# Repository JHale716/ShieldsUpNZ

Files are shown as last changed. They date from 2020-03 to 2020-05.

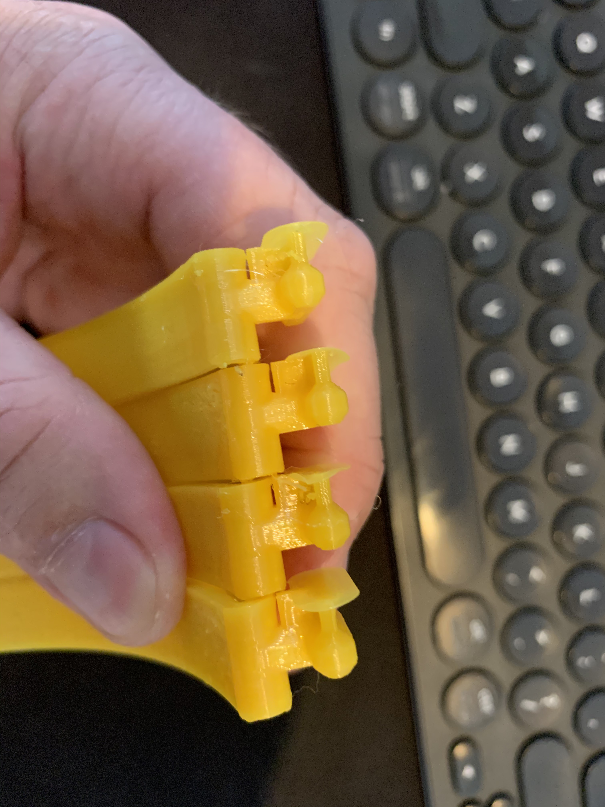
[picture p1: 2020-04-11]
6. Images/Ender3 Printing/V2 Support gap 1.jpeg

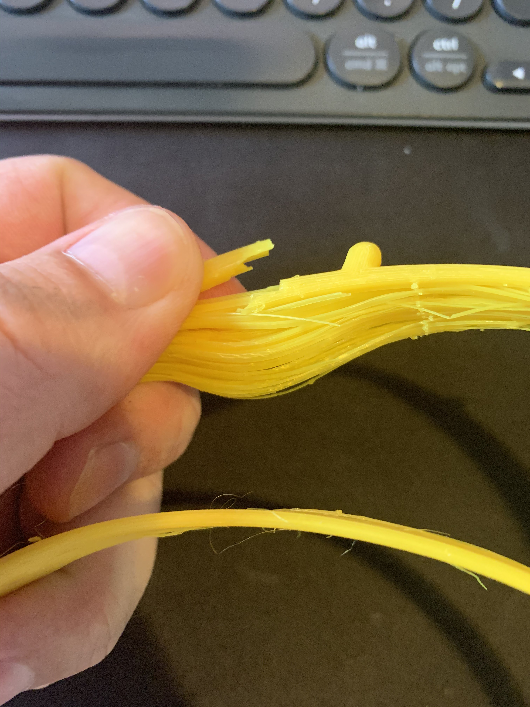
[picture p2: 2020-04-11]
6. Images/zRandom/Extrusion issues.jpeg

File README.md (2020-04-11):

# ShieldsUp Repository 
#### 3D print files and instructions to facilitate production of face shields for medical support purposes in the Covid-19 crisis

## Give-A-Little
Please help spread the word on your social media by posting the link. The more we have donated, the more shields we can fund for medical professionals to keep them safe so they are there to help you.
www.shieldsup.gives/give-a-little

## Medical People on the front line

### Request your shields now

If these face shields will help keep you or your people safer, then go ahead and request some now, they are free but we would really appreciate a koha donation to help cover the costs.

* If you are a medical practice and you need face shields, request them here --> https://shieldsup.gives/request-shields
* For disinfection - The Prusa Disinfection Guide is here --> http://www.shieldsup.gives/disinfection

## For Team Members 

* If you are a team member and need access to the webapp, request that here --> https://shieldsup.gives/WebApp
* Documentation - all of the documents to put this together and make it happen, the instruction manual so to speak.
* Design Files - the raw files for the face shields, DXF files for the laser cutter.
* STL Files - the STL files you need to 3D print the frame for the shield.
* CURA Slicer FIles - sample files to get you started if you are using Ultimaker Cura Slicer software.
* GCODE Printer FIles - gcode files for the specified printers to get things going quickly for people, use at your own risk.
* Images - images of the shields being made
* Source - source files and base files where licensed material is initiall captured. 

* zArchive folders, there are a number around, these contain superceeded material for backup, version control and roll back purposes, as well as helping with the historical record of the project.

## Not a team member and what to help?

If you are interested in more information about what we are doing or you want to help out, please contact us through our website https://shieldsup.org.nz/

# Shields UP, Stay Safe!

* The Open Face Mask is licensed under a Creative Commons Attribution-NonCommercial 4.0 International License.
* COVID-19 Face Shield is licensed under a Creative Commons Attribution-NonCommercial 4.0 International License. This version is by [Jase] on behalf of Shields Up and based on a work by Prusa Research, available at https://www.prusaprinters.org/social/16-prusa-research/prints.

* gcode files can misbehave on some machines, even when they have been created for your make and model, please watch what it is doing to ensure that it is working as expected. Do Not set and forget until you know it works correctly.
* Do Not use a gcode file from a different printer to yours you may damage your machine.
* Use at your own risk, if in doubt ask an expert!

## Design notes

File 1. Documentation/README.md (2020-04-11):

# ShieldsUp General documentation
#### for the ShieldsUp project in New Zealand

* 3D Printer Settings for Headband folder contains a variety of printer settings we have found work, they are machine dependant and may not work for your specific machine, buy they are a starting point.
* Delivery Documentation contains the documentation relating to delivering face shields.
* Disinfection contains the maker post production disinfection guides.
* Headstrap Documentation contains images and video of the various approaches to making the elastic headband.
* MoH PPE Giude, is the PDF material from the Ministry of Health on the use and management of Personal Protective Equipment.
* Visor Documentation, information on the three visor approaches, Manual, A4 clear sheet, & Laser Cut which is the preferred option
* Webapp Documentation, user support for the Shields Up WebApp for managing logistics of the project.

* zArchive folders, there are a number around, these contain superceeded material for backup, version control and roll back purposes, as well as helping with the historical record of the project.

## Give-A-Little
Please help spread the word on your social media by posting the link. The more we have donated, the more shields we can fund for medical professionals.
www.shieldsup.gives/give-a-little

### Links to places you may be looking for

* If you are a medical practice and you need face shields, request them here --> https://shieldsup.gives/request-shields
* If you are a team member and need access to the webapp, request that here --> https://shieldsup.gives/WebApp
* The Prusa Disinfection Guide is here --> http://www.shieldsup.gives/disinfection

## Not a team member and what to help?

If you are interested in more information about what we are doing or you want to help out, please contact us through our website https://shieldsup.org.nz/

# Shields UP, Stay Safe!

COVID-19 Face Shield is licensed under a Creative Commons Attribution-NonCommercial 4.0 International License. This version is by [Jase] on behalf of Shields Up and based on a work by Prusa Research, available at https://www.prusaprinters.org/social/16-prusa-research/prints.

* gcode files can misbehave on some machines, even when they have been created for your make and model, please watch what it is doing to ensure that it is working as expected. Do Not set and forget until you know it works correctly.
* Do Not use a gcode file from a different printer to yours you may damage your machine.
* Use at your own risk, if in doubt ask an expert!

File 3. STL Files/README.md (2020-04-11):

# ShieldsUp Repository 
#### 3D print files 

## Give-A-Little
Please help spread the word on your social media by posting the link. The more we have donated, the more shields we can fund for medical professionals to keep them safe so they are there to help you.
www.shieldsup.gives/give-a-little

## Medical People on the front line

### request your shields now

If these face shields will help keep you or your people safer, then go ahead and request some now, they are free but we would really appreciate a koha donation to help cover the costs.

* If you are a medical practice and you need face shields, request them here --> https://shieldsup.gives/request-shields
* The Prusa Disinfection Guide is here --> http://www.shieldsup.gives/disinfection

## For Team Members 

* If you are a team member and need access to the webapp, request that here --> https://shieldsup.gives/WebApp

These STL files are the current design files needed to 3D print the headband

* The Core files you need are in ShieldsUpProject
* Shieled Jig is for a jig used to drill holes for visors
* Prusa Faceshield Cover is a cover for the top of the headband to close in the gap, not generally required, some hospitals potentially will request these to be added.   

## Not a team member and what to help?

If you are interested in more information about what we are doing or you want to help out, please contact us through our website https://shieldsup.org.nz/

# Shields UP, Stay Safe!

COVID-19 Face Shield is licensed under a Creative Commons Attribution-NonCommercial 4.0 International License. This version is by [Jase] on behalf of Shields Up and based on a work by Prusa Research, available at https://www.prusaprinters.org/social/16-prusa-research/prints.

* gcode files can misbehave on some machines, even when they have been created for your make and model, please watch what it is doing to ensure that it is working as expected. Do Not set and forget until you know it works correctly.
* Do Not use a gcode file from a different printer to yours you may damage your machine.
* Use at your own risk, if in doubt ask an expert!

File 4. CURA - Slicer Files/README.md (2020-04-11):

# ShieldsUp
#### Arranged by printer type to facilitate novice users getting going quickly

Format of file names to maintain sense, and sorting:
* Machine Code -Cura assigns three characters, i.e. Creality Ender 3 -> CE3_ (we need this so we know what multiple files names the same are for)
* File_Name_Printed_
* Layer Height_
* Infill Setting_
* Adhesion (N=none, S=Skirt, B=Brim, R=Raft)

ie. CE3_Shields_Up_Project_-_SUP_V1.2_0.2_N.

# Shields UP, Stay Safe!

COVID-19 Face Shield is licensed under a Creative Commons Attribution-NonCommercial 4.0 International License. This version is by [Jase] on behalf of Shields Up and based on a work by Prusa Research, available at https://www.prusaprinters.org/social/16-prusa-research/prints.

* gcode files can misbehave on some machines, even when they have been created for your make and model, please watch what it is doing to ensure that it is working as expected. Do Not set and forget until you know it works correctly.
* Do Not use a gcode file from a different printer to yours you may damage your machine.
* Use at your own risk, if in doubt ask an expert!

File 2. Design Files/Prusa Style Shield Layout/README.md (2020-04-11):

# ShieldsUp

Chris Metcalfe  9:07 AM 30/3/2020
Hey guys. Geting serious about the visors here for a second. Please see files attached to this post for nested shared line DXF files suitable for laser cutting for the Prusa style shield frame.
I have created two versions of each for both 0.5mm PetG and 0.75mm PetG. The only difference is with the 0.75mm file i have moved the outside holes out by 0.5mm to make it easier to fit onto the Prusa style frame.
2440x1220 full size sheet will yield 50 visors
800x1220 will yield 15 visors (45 per sheet)
Use them, share them.

# Shields UP, Stay Safe!

COVID-19 Face Shield is licensed under a Creative Commons Attribution-NonCommercial 4.0 International License. This version is by [Jase] on behalf of Shields Up and based on a work by Prusa Research, available at https://www.prusaprinters.org/social/16-prusa-research/prints.

* gcode files can misbehave on some machines, even when they have been created for your make and model, please watch what it is doing to ensure that it is working as expected. Do Not set and forget until you know it works correctly.
* Do Not use a gcode file from a different printer to yours you may damage your machine.
* Use at your own risk, if in doubt ask an expert!

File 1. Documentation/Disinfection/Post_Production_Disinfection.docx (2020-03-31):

Post Production Disinfection

Before sending your 3D printed shields to their final destination they must be disinfected to remove any possible contaminants. Gloves should be worn to prevent recontamination.

- To begin with start by wiping down a bench with a surface disinfectant and allow to dry, put down some paper towels to stop your shields getting damaged.
- Fill a bucket/tub with 10L of warm water, add 30mL of dishwashing liquid and stir to combine
- Wash shields with a clean soft cloth in the soapy water and then rinse off in cold water
- Set down on the paper towels
- Wipe down shields with a paper towel to remove excess water
- Spray with isopropyl alcohol and allow to air dry

Once the shields are dry they are ready to be packaged and sent out to frontline workers.

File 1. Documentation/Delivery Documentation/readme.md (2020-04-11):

# Delivery documentation for printing

File | Details | Size
----- | ----- | -----
Info Card.pdf | Basic info card | 75x52mm 
Shield Hand Out.pdf | Detailed delivery hand out | A4
cards20upA3.pdf | 20x delivery cards | A3
cards9upA4.pdf | 9x delivery cards | A3
postersA4x2upA3.pdf | 2x A4 posters | A3
postersA5x2upA4.pdf | 2x A5 posters | A4
shieldsup-identifiers.pdf | 1x delivery card and 1x A5 poster for car windscreen | 320x284mm

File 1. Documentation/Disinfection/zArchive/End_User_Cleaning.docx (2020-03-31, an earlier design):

End User Cleaning & Instructions For Use

Thank you for choosing to use Shields Up to protect your frontline staff. These items have been disinfected prior to being sent out to prevent any potential spread of biological contaminants.

The shields are comprised of three parts:

- Plastic visor (single patient use)
- Main shield component
- Elastic backstrap

The plastic visor is single patient use and must be disposed of between cases.

The main shield component, and elastic backstrap are reusable.

Cleaning between cases:

Discard the visor. Wipe down shield components with 70% isopropyl alcohol wipes. If your facility does not have 70% isopropyl alcohol wipes, then it is acceptable to use a paper towel laden with 70% isopropyl alcohol.

End of day cleaning:

Fill a sink with 10L of warm water and add 30mL of cleaning solution such as Matrix® or Sonidet®. Clean shield components fully submerged with a soft cloth. Rinse off with cold water then wipe off excess water with a lint free cloth or paper towel. Leave elastic back strap to air dry overnight. Use a 70% isopropyl alcohol wipe to remove any remaining water and allow to stand overnight.

Exposure to temperatures greater than 70 degrees Celsius will lead to degradation and potential failure of the shields. DO NOT machine wash, hand wash ONLY.

Shields Up NZ is not responsible for any damage/harm to property or persons as a result of not complying with these IFU’s.

For any questions please contact:

dominic@shieldsup.org.nz

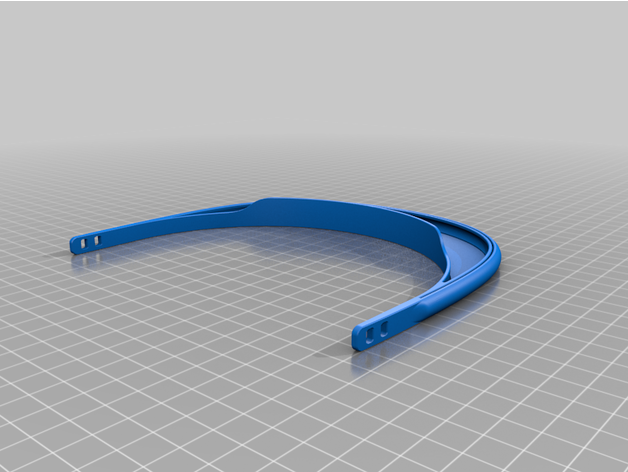
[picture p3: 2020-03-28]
1. Documentation/zVisera_Plana Design/Visera_Plana_con_cierre_y_ventilacion_0.5.png

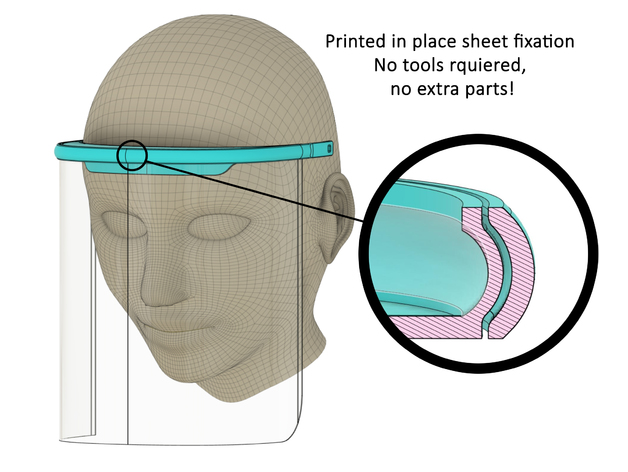
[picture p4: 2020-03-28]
1. Documentation/zVisera_Plana Design/plana.jpg

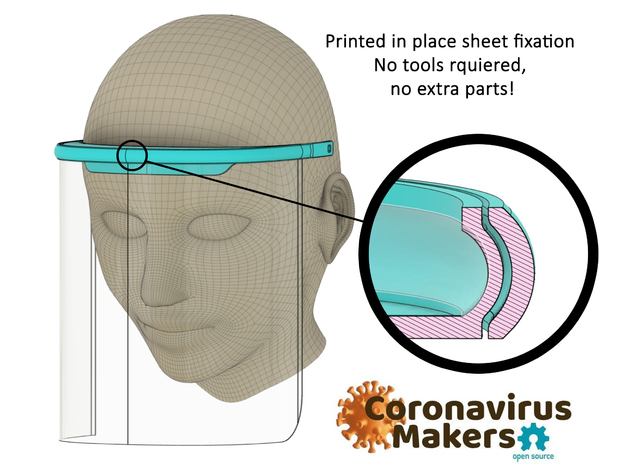
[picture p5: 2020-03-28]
1. Documentation/zVisera_Plana Design/plana_2.jpg

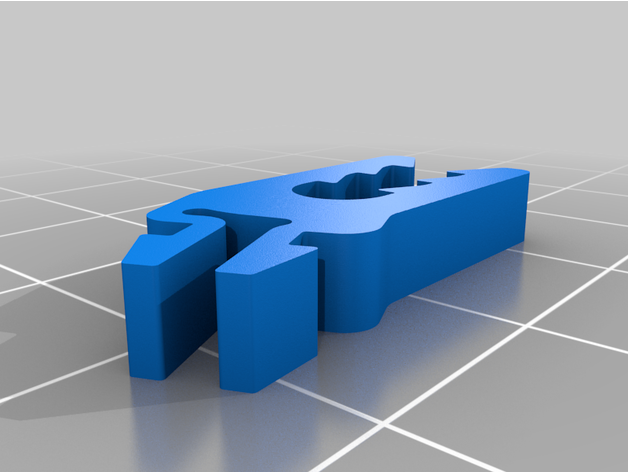
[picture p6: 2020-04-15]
8. Other Projects/Visor shield for caps/7. Images/cliplateral2.png

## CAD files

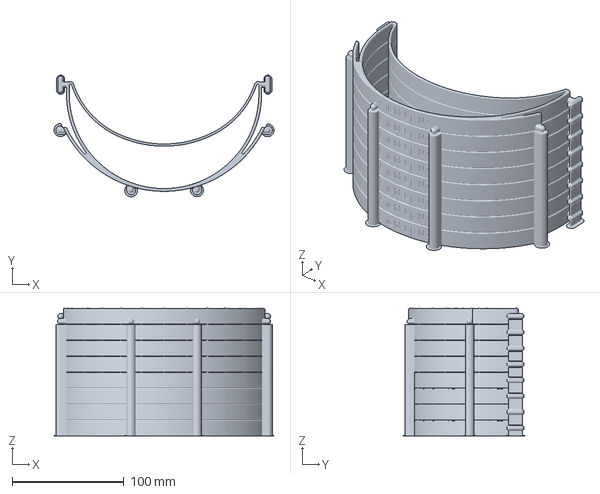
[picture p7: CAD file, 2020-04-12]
4. CURA - Slicer Files/Prusa/MK3/MK3_SUP V2.1 - 8xStack_0.25_if(prusadefault)_none_PETg_9h21mins_E-265C_B-85C(1st layer)_B-90C(remaining).3mf
197.3 x 109.1 x 114.6 mm

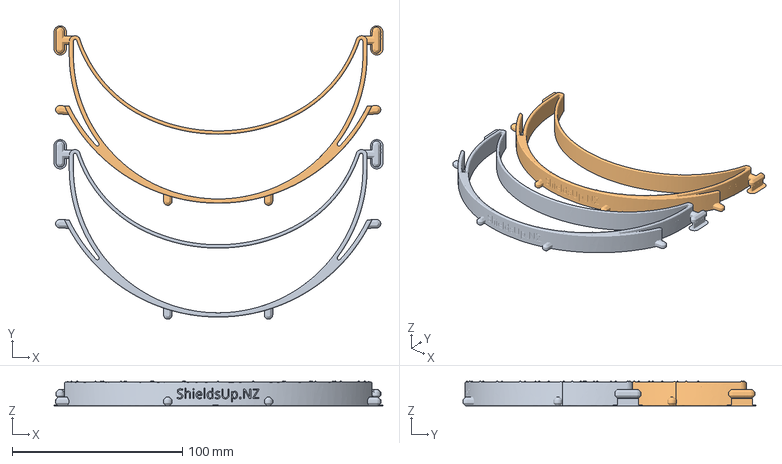
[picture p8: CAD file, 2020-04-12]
4. CURA - Slicer Files/Prusa/MK3/MK3_SUP V2.1 - 2xFlat_0.25_if(prusadefault)_none_PETg_9h21mins_E-265C_B-85C(1st layer)_B-90C(remaining).3mf
193.2 x 172.4 x 14.4 mm

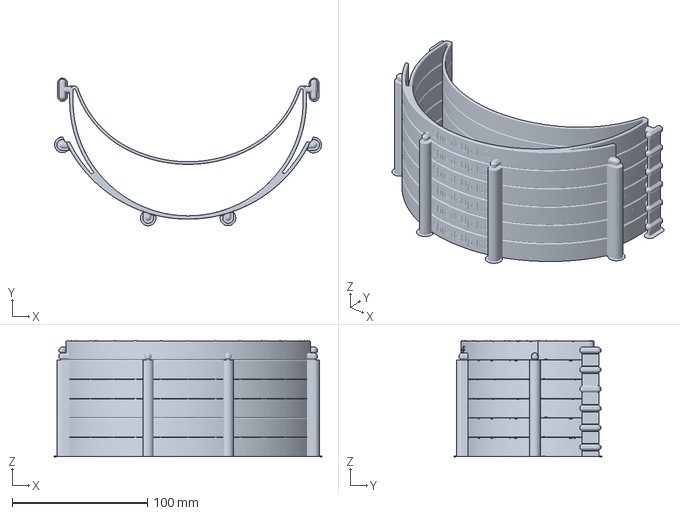
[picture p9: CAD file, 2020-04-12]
4. CURA - Slicer Files/Prusa/MK3/MK3_SUP V2.1 - 6xStack_0.25_if(prusadefault)_none_PETg_9h21mins_E-265C_B-85C(1st layer)_B-90C(remaining).3mf
197.3 x 109.1 x 86.0 mm

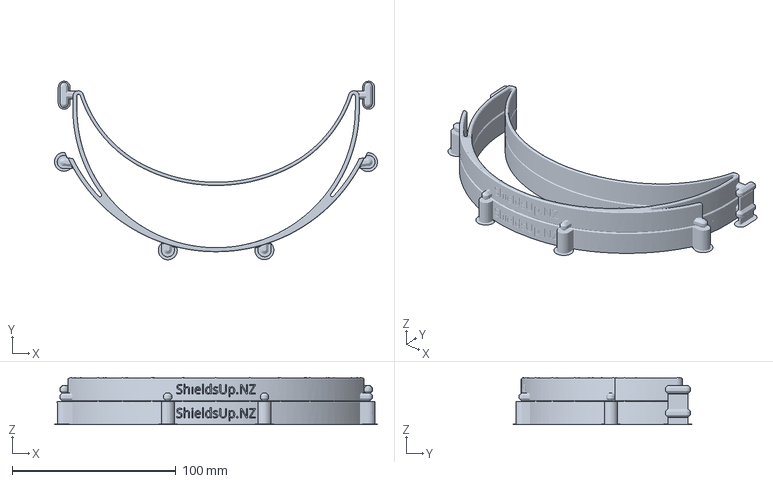
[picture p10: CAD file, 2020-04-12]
4. CURA - Slicer Files/Prusa/MK3/MK3_SUP V2.1 - 2xStack_0.25_if(prusadefault)_none_PETg_9h21mins_E-265C_B-85C(1st layer)_B-90C(remaining).3mf
197.3 x 109.1 x 28.8 mm

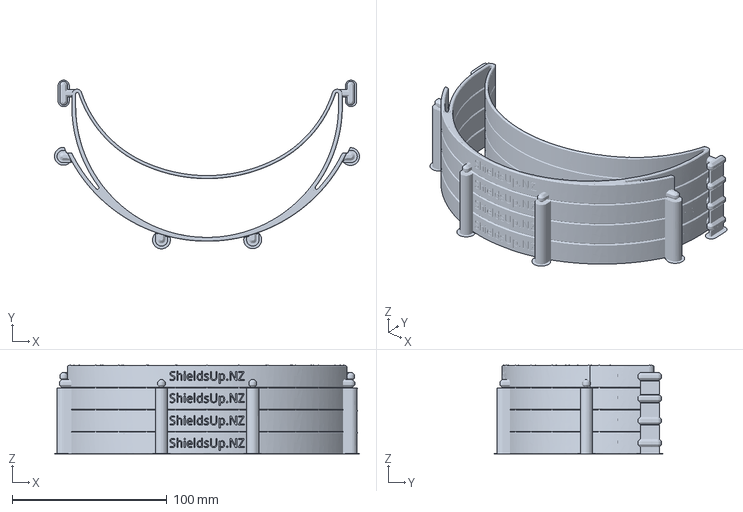
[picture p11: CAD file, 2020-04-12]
4. CURA - Slicer Files/Prusa/MK3/MK3_SUP V2.1 - 4xStack_0.25_if(prusadefault)_none_PETg_9h21mins_E-265C_B-85C(1st layer)_B-90C(remaining).3mf
197.3 x 109.1 x 57.4 mm

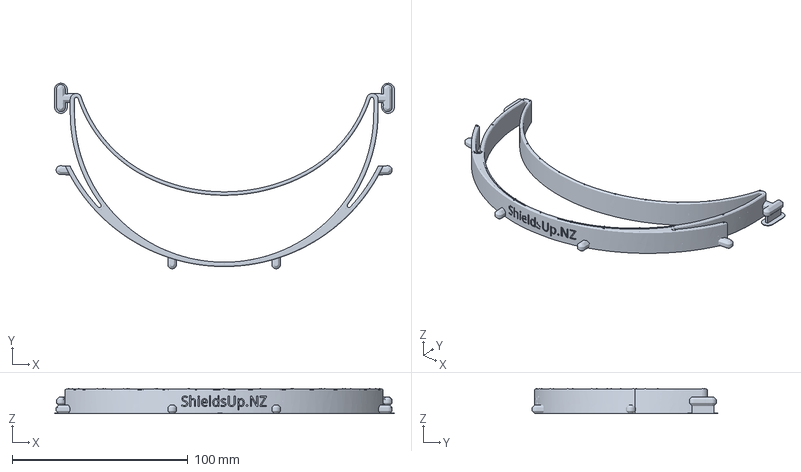
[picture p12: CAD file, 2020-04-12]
4. CURA - Slicer Files/Prusa/MK3/MK3_SUP V2.1_0.25_if(prusadefault)_none_PETg_9h21mins_E-265C_B-85C(1st layer)_B-90C(remaining).3mf
193.2 x 105.5 x 14.4 mm

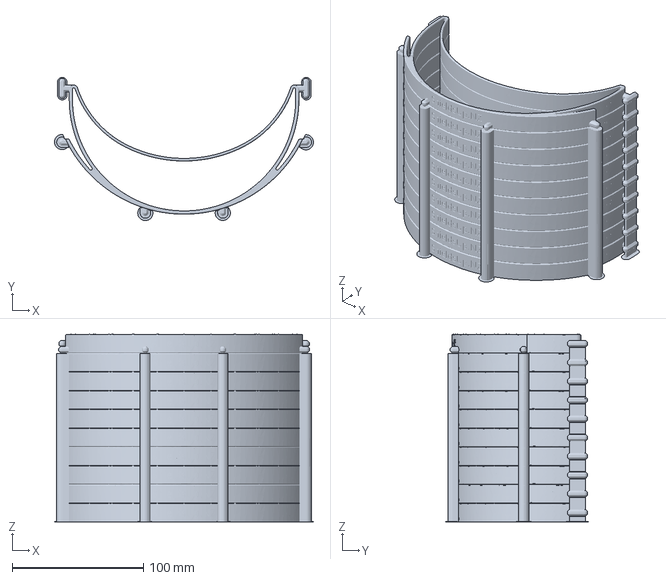
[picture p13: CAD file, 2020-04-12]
4. CURA - Slicer Files/Prusa/MK3/MK3_SUP V2.1 - 10xStack_0.25_if(prusadefault)_none_PETg_9h21mins_E-265C_B-85C(1st layer)_B-90C(remaining).3mf
197.3 x 109.1 x 143.2 mm

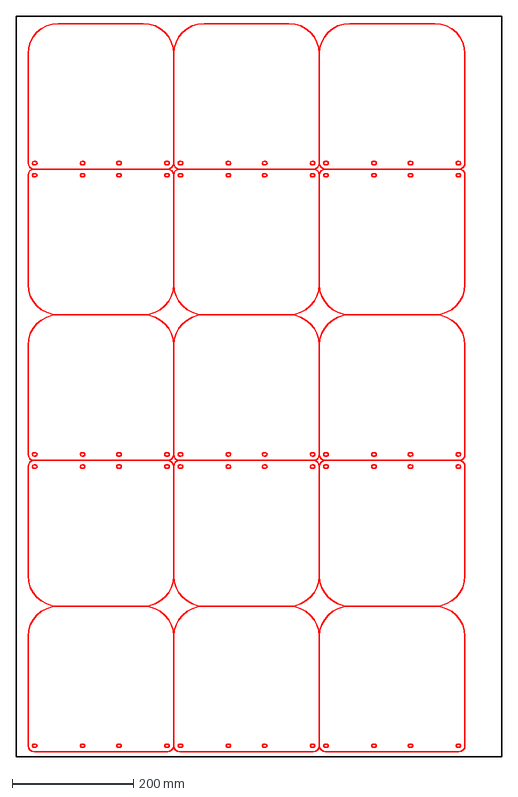
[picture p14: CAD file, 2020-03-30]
2. Design Files/Prusa Style Shield Layout/Shield Array Shared Line_0.50_15 Visors_800x1220_B.dxf
800.0 x 1220.0 mm

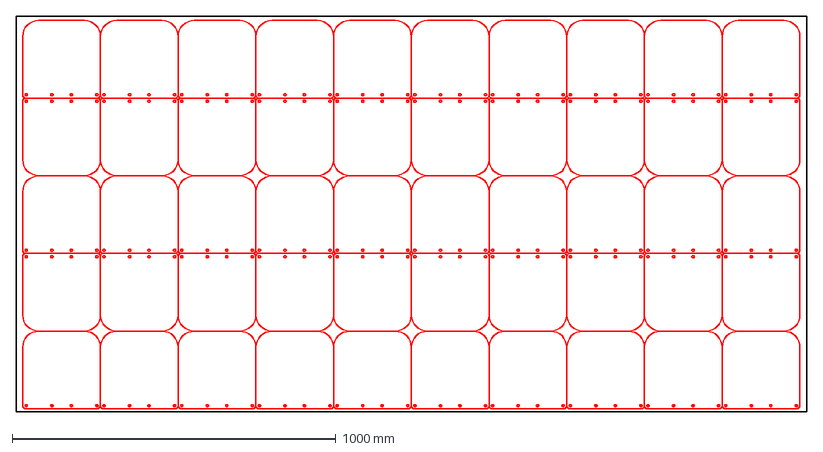
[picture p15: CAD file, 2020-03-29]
2. Design Files/Prusa Style Shield Layout/zPrior Versions/Shield Array Shared Line_0.50_50 Visors_2440 x 1220.DXF
2440.0 x 1220.0 mm

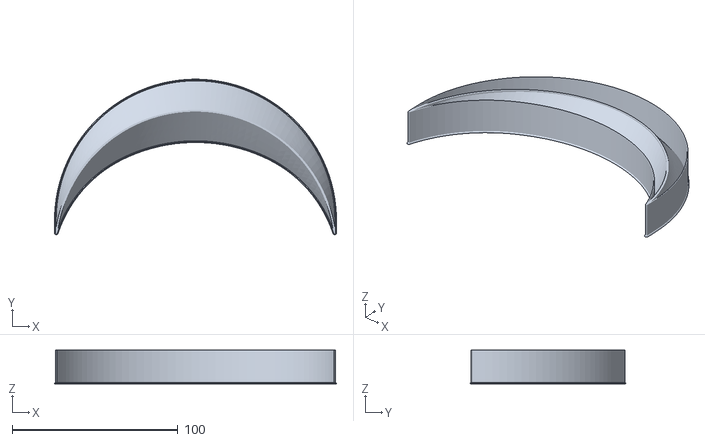
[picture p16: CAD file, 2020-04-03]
3. STL Files/Prusa Faceshield Cover/prusa_protective_face_shield_cover_rc1.stl
170.2 x 93.9 x 20.5

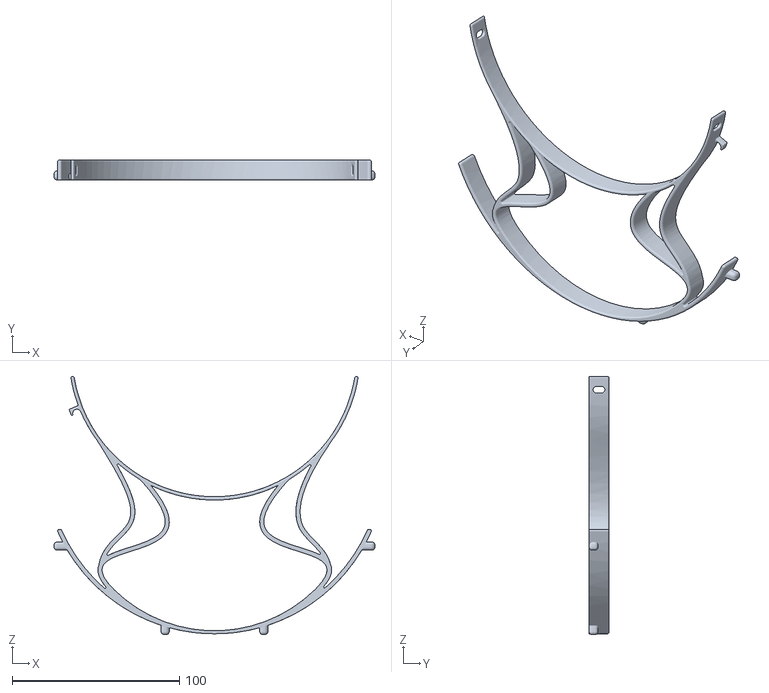
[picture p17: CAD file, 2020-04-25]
3. STL Files/ShieldsUp-Dental Version/V5.1Dental.STL
192.0 x 12.0 x 154.5

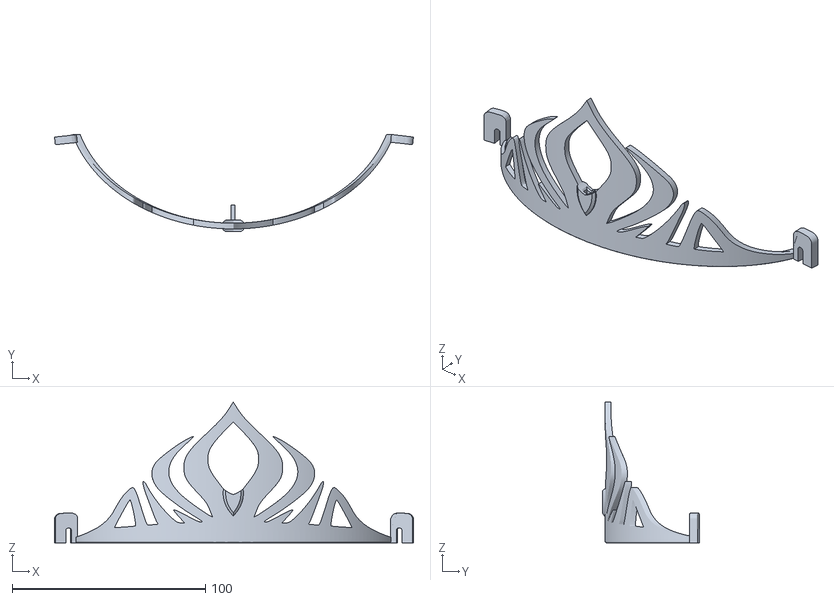
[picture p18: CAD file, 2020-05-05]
3. STL Files/Tiara for Faceshield/Tiara_addon.stl
185.8 x 50.4 x 72.8

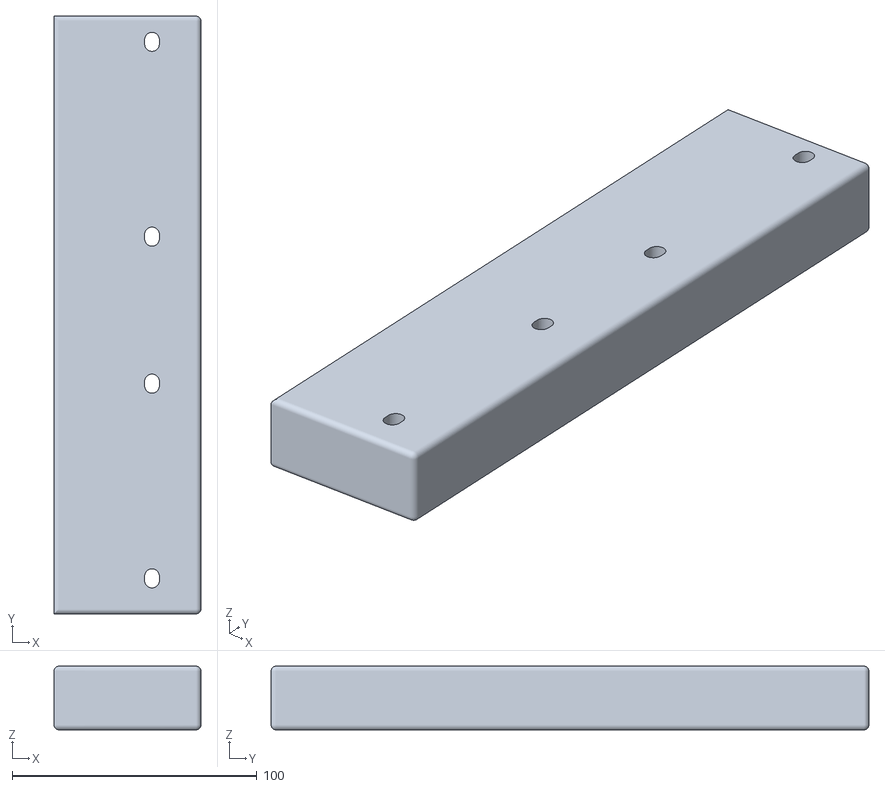
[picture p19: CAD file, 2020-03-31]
3. STL Files/Visor Jig/Visor_Hole_Jig.STL
60.0 x 244.0 x 26.0

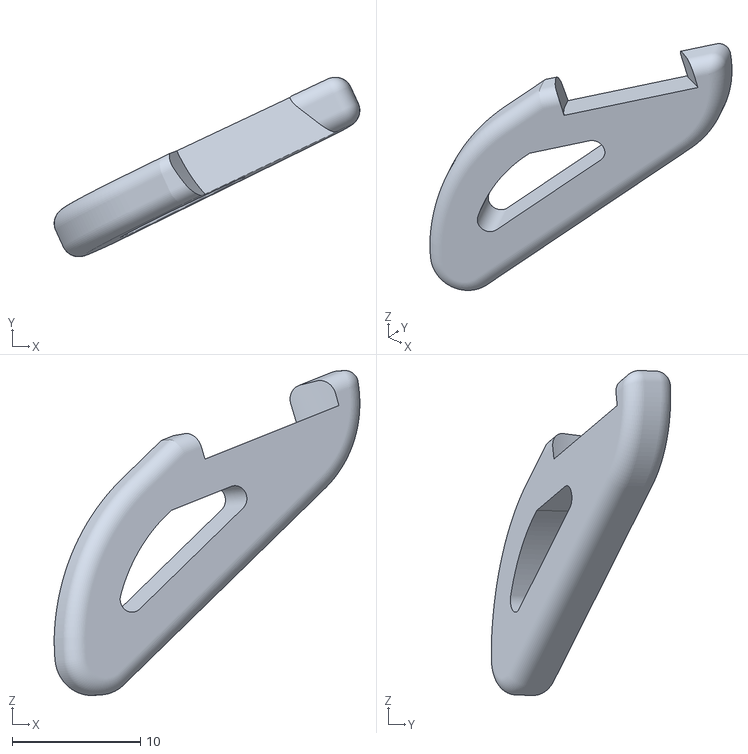
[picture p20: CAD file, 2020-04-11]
8. Other Projects/Open Face Mask/3. STL Files/nosespacer R.stl
23.8 x 14.0 x 25.3

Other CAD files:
3. STL Files/ShieldsUpProject/SUP V2.1-b - 4xStack.stl
4. CURA - Slicer Files/Creality/Ender3/CE3_V5.1Dental_0.27_if0_N_PETg.3mf
8. Other Projects/Open Face Mask/5. CURA - Slicer Files/OFM-1 Cura Project.3mf
8. Other Projects/Visor shield for caps/2. Blend - Edited Files/Lateral.stp
2. Design Files/Prusa Style Shield Layout/Shield Array Shared Line_0.50_50 Visors_2440 x 1220_B.dxf
2. Design Files/Prusa Style Shield Layout/Shield Array Shared Line_0.75_15 Visors_800x1220_B.dxf
2. Design Files/Prusa Style Shield Layout/Shield Array Shared Line_0.75_50 Visors_2440 x 1220_B.dxf
2. Design Files/Prusa Style Shield Layout/zPrior Versions/Shield Array Shared Line_0.50_15 Visors_800x1220.dxf
2. Design Files/Prusa Style Shield Layout/zPrior Versions/Shield Array Shared Line_0.75_15 Visors_800x1220.dxf
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

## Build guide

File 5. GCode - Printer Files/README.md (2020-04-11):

# ShieldsUp GCODE Files
### Arranged by printer type to facilitate novice users getting going quickly

## Format of file names to maintain sense, and sorting:

* _Machine Code_ -Cura assigns three characters, i.e. Creality Ender 3 -> CE3 (we need this so we know what multiple files named the same are for)
* _File Name Printed_
* _Xup_ (number of frames in the print, omitted equals 1) 
* _Layer Height_
* _Infill Setting_
* _Adhesion_ (none, skirt, brim, raft)
* _Filament Type_
* _Speed_
* _Hours Minutes_
* _E-TempC_ Extruder Temp
* _B-TempC_ Bed/Base Temp

ie. CE3_SUP_V2.1-b_2up_0.27_if0_none_PLA_60mm-s_4h58mins_E-215C_B-62C.gcode
* Creality Ender 3
* SUP_V2.1-b (b=brim on supports, n=no brim on supports) 
* 2 Frames in the print
* 0.27mm layer height
* Infill 0%
* No bed adhesion
* PLA filament
* 60mm/s print speed
* 4hours 58 minutes expected print time. 
* Extruder at 215degC
* Base/Bed at 62degC

## If you are using Cura
A useful plugin for the Cura slicer that will assist in keeping track of gcodes you produce.

Install the plugin Gcode filename format plugin. In the market place top right of your screen.
After install and restart it will appear in your extensions menu.

This configuration will give you the filing format we're asking for in the GitHub Repo, when you select the plugin and "Edit Format" and paste this in -> [base_name]_[layer_height]_if[infill_sparse_density]_[adhesion_type]_[material]_[speed_print]mm-s_[print_time_hours]h[print_time_minutes]mins_E-[material_print_temperature]C_B-[material_bed_temperature]C

If you have working gcodes and you're on printers other than the UM2/UM2+/ UM5, Ender 3/3Pro, please send J-P Hale a copy in Slack so we can load into GitHub for newbies to help get them going quicker. 

# Shields UP, Stay Safe!

COVID-19 Face Shield is licensed under a Creative Commons Attribution-NonCommercial 4.0 International License. This version is by [Jase] on behalf of Shields Up and based on a work by Prusa Research, available at https://www.prusaprinters.org/social/16-prusa-research/prints.

* gcode files can misbehave on some machines, even when they have been created for your make and model, please watch what it is doing to ensure that it is working as expected. Do Not set and forget until you know it works correctly.
* Do Not use a gcode file from a different printer to yours you may damage your machine.
* Use at your own risk, if in doubt ask an expert!

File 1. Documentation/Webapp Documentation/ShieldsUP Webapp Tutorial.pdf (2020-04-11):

# Tutorial for ShieldsUP webapp

### Link: https://app.shieldsup.org.nz

- NOTE: We are still marking orders as complete from different sources. Hub Coordinators - If you know of orders that have been sent out already, please mark them as shipped

# How to obtain access

- Either use the login request form at https://forms.gle/eBnd5k1sVXNhMdmE9
- or DM Rohan Fletcher on Slack
- Note: you will need to be on Slack to obtain a login

# How to find orders to fill

1) Click Orders
2) Filter by Waiting state

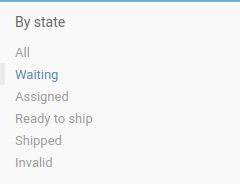
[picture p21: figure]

3) Filter by delivery city

4) The resulting list

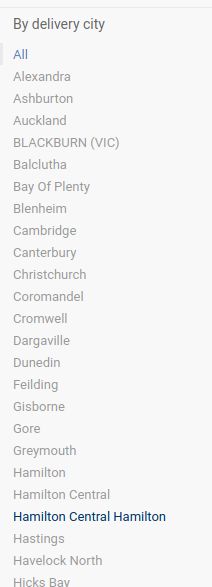
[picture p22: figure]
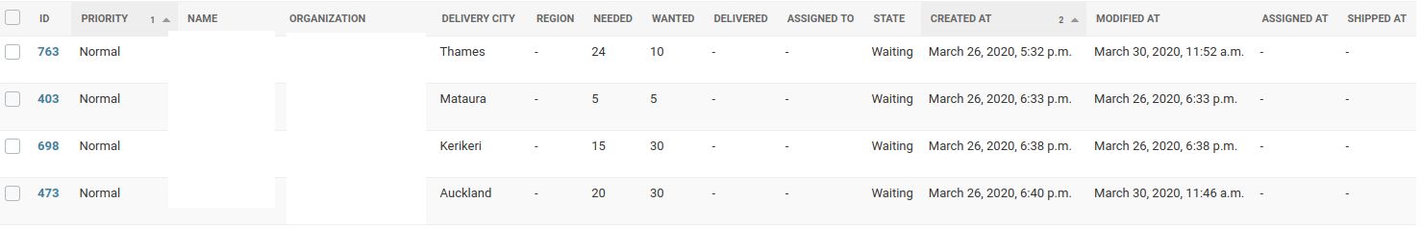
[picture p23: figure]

5) Click on the ID you want to assign

6) You can see the order details - scroll down past the top fields

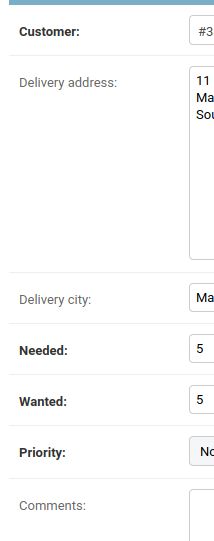
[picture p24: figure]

7) Look for the Manufacturing info section

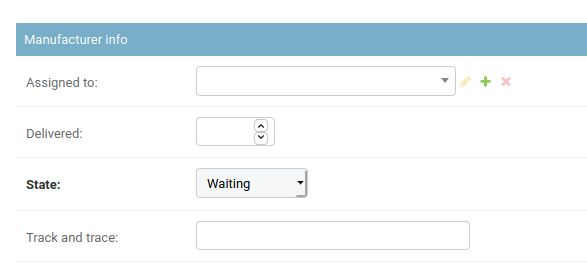
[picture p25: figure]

8) Click the dropdown next to Assigned to, then select an entry (type part of a name to filter the options)

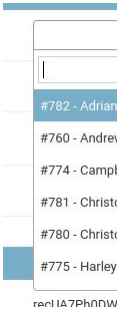
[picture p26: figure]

9) Change state to Assigned
10) Click SAVE

11) END STEPS

# How to see orders assigned to yourself

Note: you will need to have a manufacturer assigned to your user to use this feature (see FAQ or guide below)

1) Go to Orders table
2) Filter state by Assigned for orders that are not complete

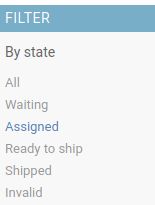
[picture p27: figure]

3) Filter assignment as Assigned to me
4) END STEPS

# What to do when you are ready to ship an order

1) Open the order that you want to ship
2) Under Manufacturing Info section, enter the amount you are delivering in Delivered
3) Change the state to Shipped
4) Click SAVE at the bottom right of the page

# How do I add a manufacturer? (HUB COORDINATORS ONLY)

1) Click Add next to Manufacturers
2) Fill in the details (please try and fill the address field as well)
3) If you want to assign a user to the manufacturer, under the System section select a user using the dropdown box

# FAQs

How do I attach a manufacturer to my user if I am not a Hub Coordinator
- NEW: When you request the login via the form, the manufacturer is automatically set up for you. If its not (you won’t show up in the attach to field), talk to your Hub Coordinator or Rohan on Slack
My order is missing from the list. What happened to it?
- Some orders were rejected in the migration from airtable. These items are in a seperate table and are currently being dealt with
Lets say I have 100 quantity on an order that I want to assign to several manufacturers. How do I do this?
- Currently it is only possible to assign one manufacturer to an order. We are looking at changing this in the near future, but for now I suggest that the Hub coordinator assigns the Hub as manufacturer and then just handle the organizing of multiple people outside of the webapp
How do I change my password?
- Top right once you are logged in there is a change password option

How do I reset my password?
- Talk to Rohan on Slack or another admin

Future Development
- Geolocation
- Statistics endpoint for websites
- Machine inventory
- 3d printers with filament diameter
- Stock of consumables and end products
- Suppliers
- Keep track of suppliers

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
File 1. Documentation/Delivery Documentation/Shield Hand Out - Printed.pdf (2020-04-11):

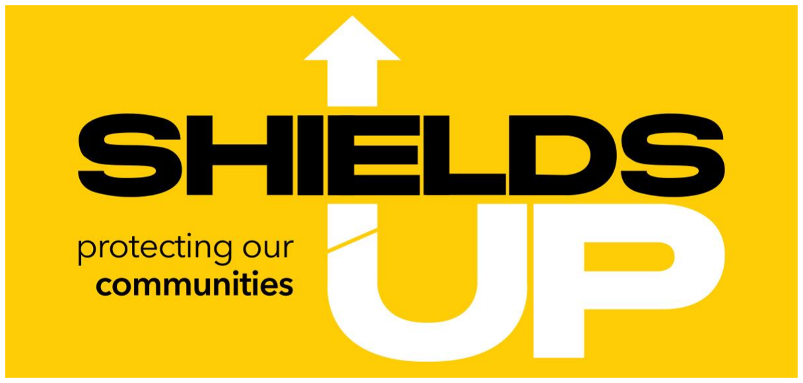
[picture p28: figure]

Give-A-Little | Disinfecting Guide | Request Shields Form
www.shieldsup.gives/give-a-little | www.shieldsup.gives/Disinfection www.shieldsup.gives/request-shields

Hello medical people of awesomeness!

Along with the rest of the nation, we thank you for continuing to look after us.

Kia kaha

A few points to note about the shields:

Please use only where absolutely necessary. Ideally the face shields would be single use, but we are flooded with requests for shields. Our challenge now is going to be keeping enough production rolling over to fulfill as many requests as possible. If you are comfortable to disinfect and re-use them that would help the wider community to get access to face shields.

These have not been sterilised - Disinfect before use. We figured you are the experts and wanted you to be comfortable with your own sterilisation methods should you choose to do that. We have taken every precaution to keep clean manufacturing environments and minimize any handling with bare hands. But please remember these have been made in people's homes, garages, offices and workshops.

They are not made from high temp plastics. The frame of these shields has been 3d printed in either PLA or PETG. If exposed to temperatures above 70°C they will become soft and start to warp. Consider this for any sterilisation method.

We are not suppliers of official medical-grade PPE. While we have blessings from various DHB’s to distribute these face shields, this initiative has no official backing by the Ministry of Health or any other government department. So please understand, these are to be used at your own risk. If you know of a contact from your DHB who may be able to offer advice, we
would love to hear from them. www.shieldsup.org.nz

We rose to action when doctors and other health professionals made the issue known in our community. Whilst totally unconventional, our network of 3d printing enthusiasts around the country is likely the best solution for providing alternative PPE shields. We are both excited and humbled to support such an effort at this time.

The Shields Up project is currently being self-funded by members of the team all around the country, like myself. We don’t expect anything in return, but if you'd like to make a Koha donation, there's a givealittle.co.nz page running, just search “makers nz covid 19 community action” or scan the QR code below.

Shields UP, Stay Safe!

Face shield design credit to Prusa Research, distributed under Creative Commons License

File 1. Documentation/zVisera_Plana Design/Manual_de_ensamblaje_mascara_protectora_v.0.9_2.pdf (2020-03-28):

# Manual de impresión y ensamblaje mascara protectora

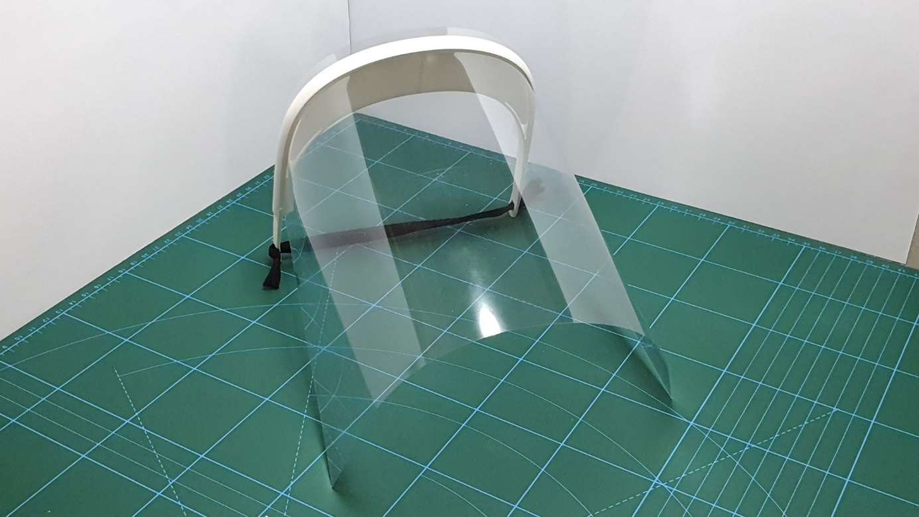
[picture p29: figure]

Página: 2/14

Página: 3/14

# Datos del Documento

Autor: | @YKA3D
Revisor: | @kermithenson
Fecha de publicación: | 18/03/2020
Observaciones:
Para comenzar a fabricar es necesario que la máquina esté correctamente calibrada. Una vez calibrada, se deberá llevar a cabo una prueba de tolerancia.

Test: https://www.thingiverse.com/thing:1662342

# Hoja de Cambios

Fecha | Versión | Autor | Cambios
18 de marzo de 2020 | v.0.1 | @YKA3D | Creación del documento
18 de marzo de 2020 | V.0.3 | @kermithenson | Modificación protocolos
20 de marzo de 2020 | V.0.9 | @YKA3D | Actualizaciones varias

# Versión STL

Fecha | Versión | Autor | Cambios
20 de marzo de 2020 | v.0.3 | @Hanochh | Creación STL mascara

Página: 4/14

# Índice

Introducción | 5
Enlace de compras | 6
Parámetros de impresión | 6
Ensamblaje de la máscara | 8

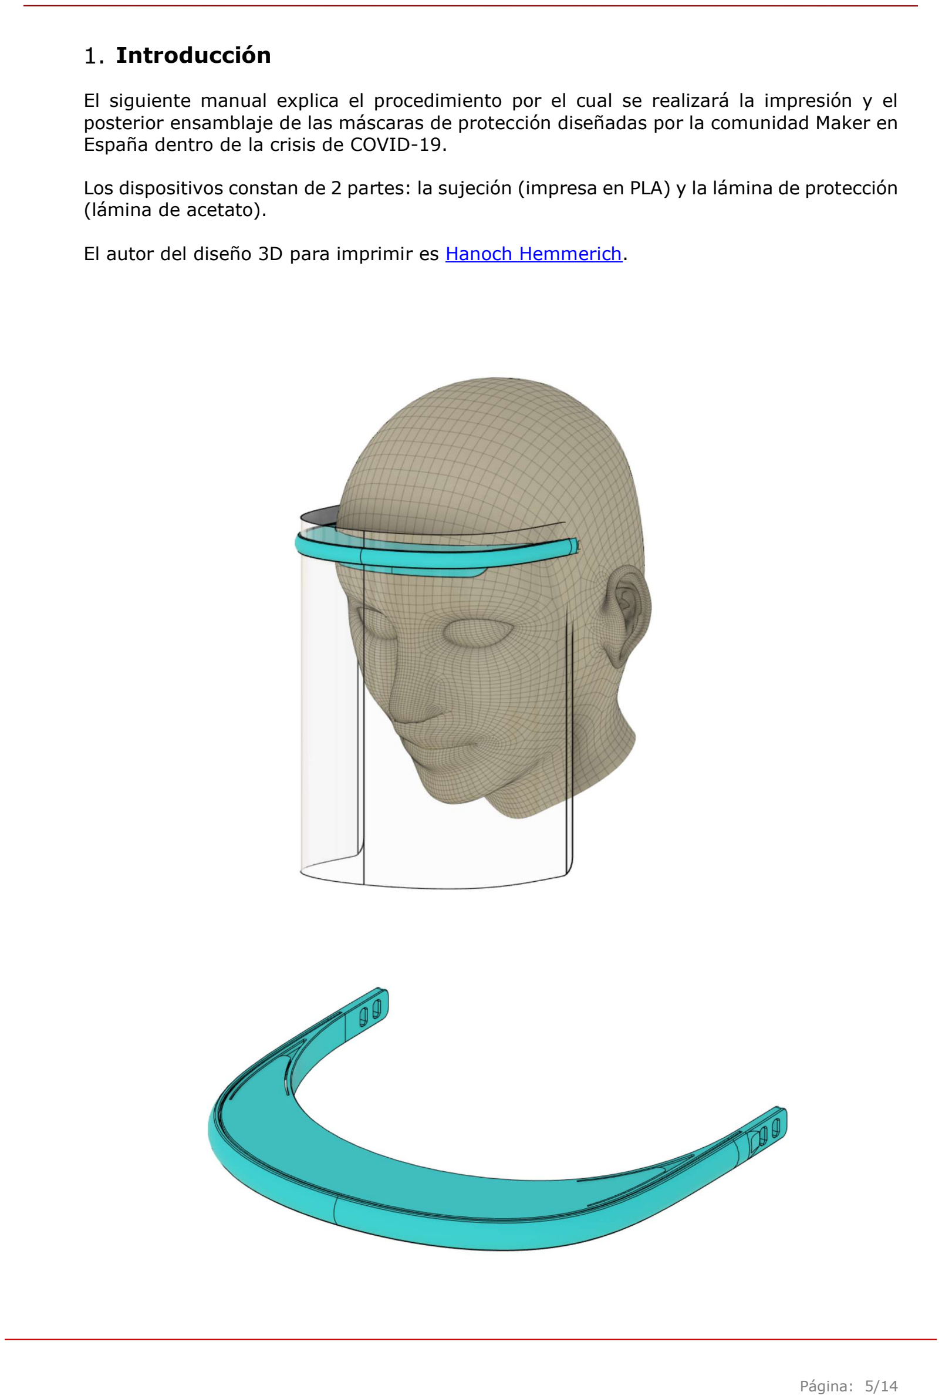
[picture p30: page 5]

Página: 5/14

### Introducción

El siguiente manual explica el procedimiento por el cual se realizará la impresión y el posterior ensamblaje de las máscaras de protección diseñadas por la comunidad Maker en España dentro de la crisis de COVID-19.

Los dispositivos constan de 2 partes: la sujeción (impresa en PLA) y la lámina de protección (lámina de acetato).

El autor del diseño 3D para imprimir es Hanoch Hemmerich.

Página: 6/14

### Enlace de compras

Los siguientes enlaces solo son una referencia del material utilizado para la elaboración de las pantallas protectoras.

- Láminas de encuadernar
o 180 micras
https://www.amazon.es/Fellowes-Cristal-Portadas-encuadernaci%C3%B3ntransparente/dp/B002BARBEK/ref=sr_1_1?__mk_es_ES=%C3%85M%C3%85%C5%BD%C3%95%C3%91&dchild=1&keywords=Fellowes+Portadas+para+encuadernar+de+PVC+transparente+180&qid=1584614023&s=office&sr=1-1
o 240 micras
https://www.amazon.es/gp/product/B000YC1UWG/ref=ppx_yo_dt_b_asin_title_o00_s00?ie=UTF8&psc=1
- Goma elástica
https://www.amazon.es/Banda-el%C3%A1stica-personalizada-Artesan%C3%ADametros/dp/B0749M5CBF/ref=sr_1_16?__mk_es_ES=%C3%85M%C3%85%C5%BD%C3%95%C3%91&crid=2QMWDSOIWQT2U&dchild=1&keywords=bobina+goma+elastica&qid=1584614347&refinements=p_85%3A831314031&rnid=831276031&rps=1&sprefix=bobina+goma+el%2Caps%2C151&sr=8-16

### Parámetros de impresión

El archivo para su impresión se puede descargar desde el siguiente enlace:

Enlace de descarga

Los parámetros de impresión solo son una guía de referencia cada uno conoce bien su máquina y los límites de esta:

- Diámetro del Nozzle: 0.4mm
- Altura de capa: 0.28mm
- Relleno: 50%
- Tipo de relleno: Rejilla
- Capas superiores: 4
- Capas inferiores: 2
- Flujo: 80%
- Sin soportes
- Velocidad de impresión:
o Perímetros: 80mm/s
o Perímetros pequeños: 80mm/s o Perímetros externos: 80mms/s o Relleno: 80mms/s
o Relleno solido: 80mms/s
o Relleno solido superior: 80mm/s o Puentes: 80mm/s
o Relleno: 80mm/s
o Recorrido: 180mm/s

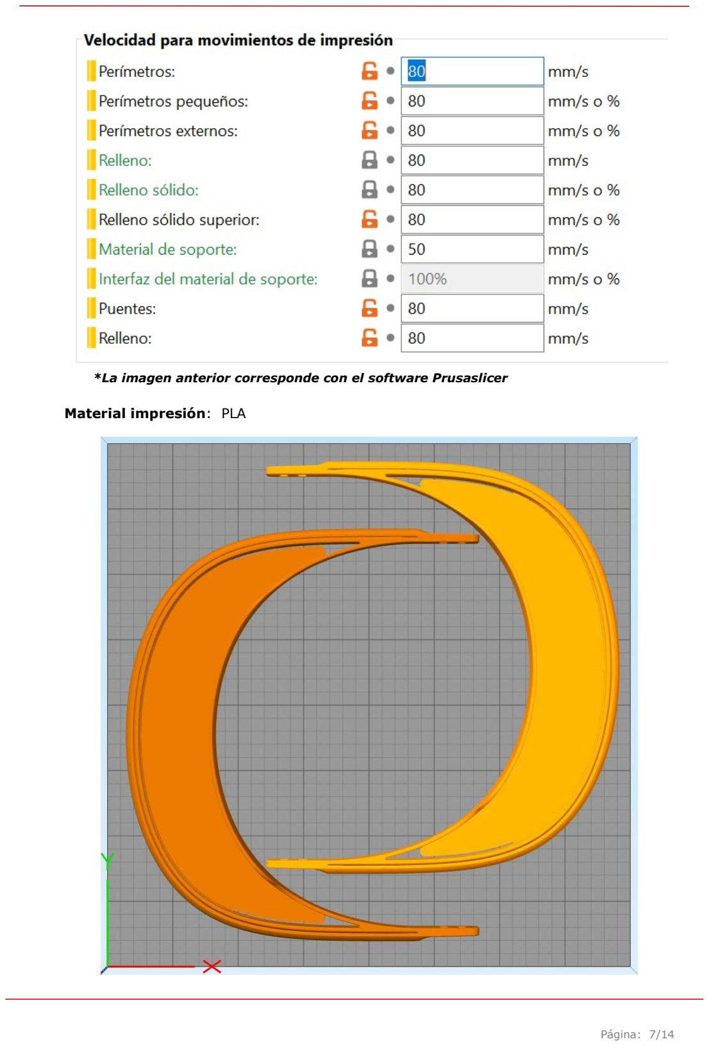
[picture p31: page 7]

Página: 7/14

*La imagen anterior corresponde con el software Prusaslicer

Material impresión: PLA

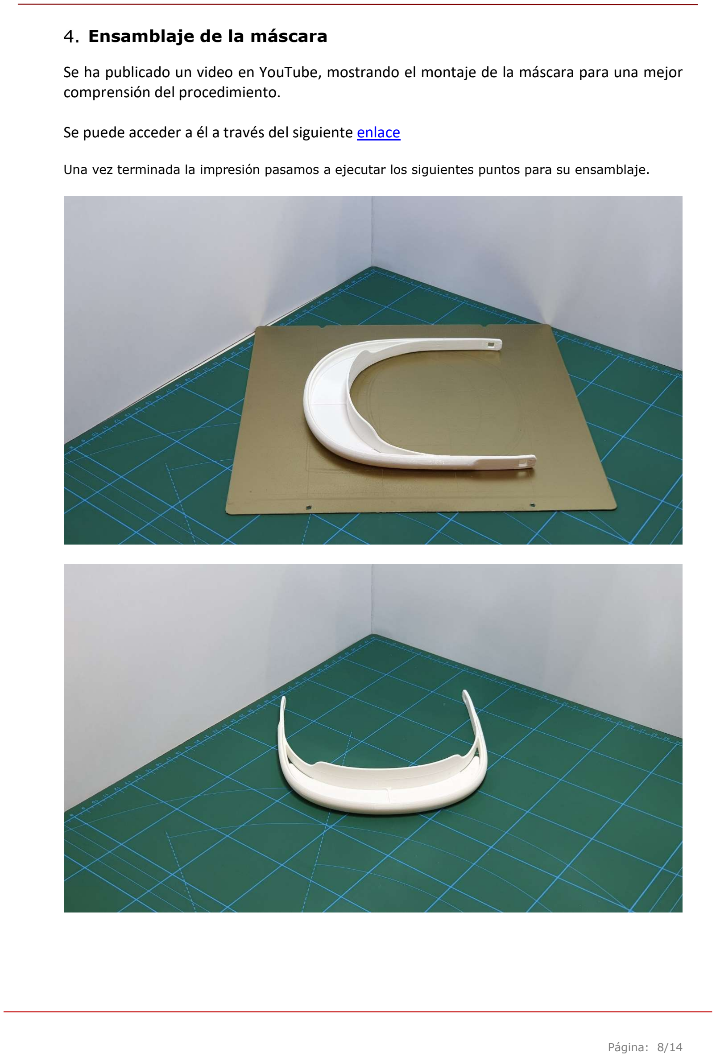
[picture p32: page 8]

Página: 8/14

### Ensamblaje de la máscara

### Se ha publicado un video en YouTube, mostrando el montaje de la máscara para una mejor

comprensión del procedimiento.

### Se puede acceder a él a través del siguiente enlace

Una vez terminada la impresión pasamos a ejecutar los siguientes puntos para su ensamblaje.

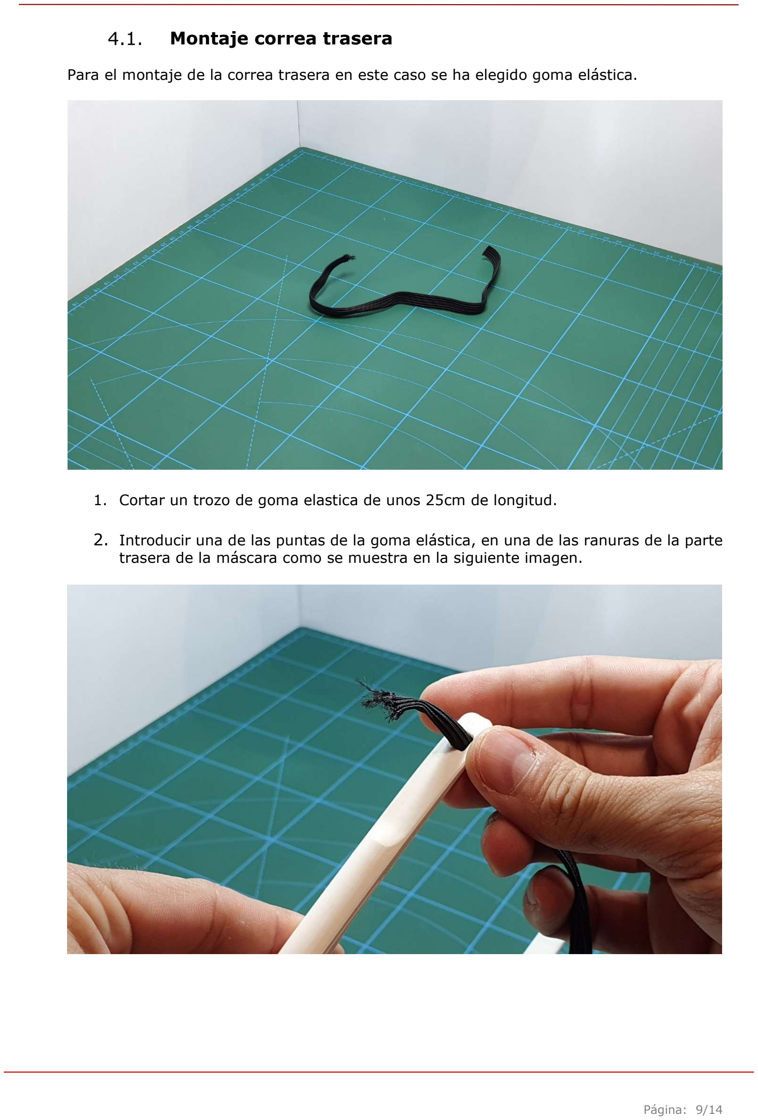
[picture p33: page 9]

Página: 9/14

### Montaje correa trasera

Para el montaje de la correa trasera en este caso se ha elegido goma elástica.

1. Cortar un trozo de goma elastica de unos 25cm de longitud.

### 2. Introducir una de las puntas de la goma elástica, en una de las ranuras de la parte

trasera de la máscara como se muestra en la siguiente imagen.

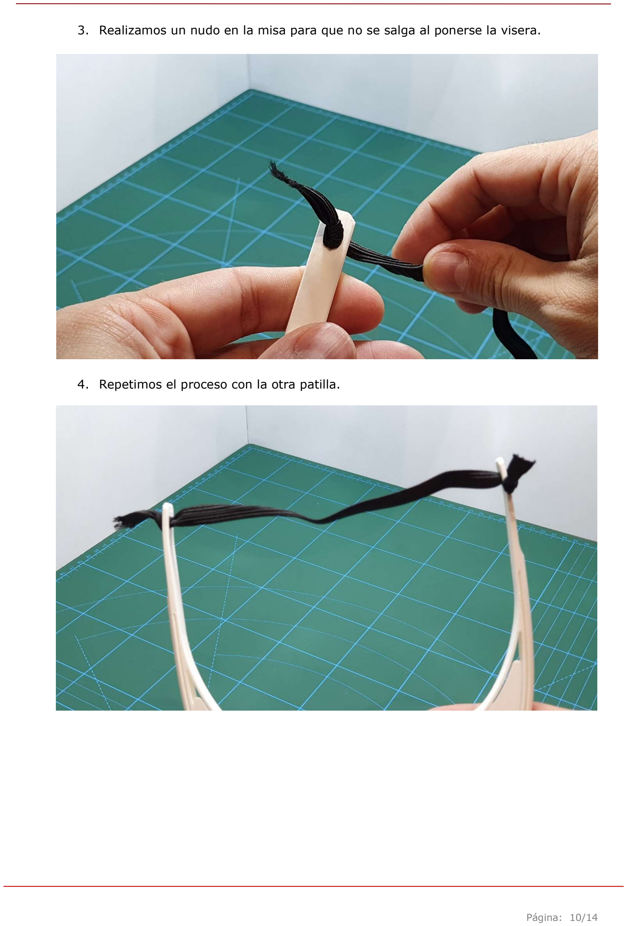
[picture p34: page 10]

Página: 10/14

3. Realizamos un nudo en la misa para que no se salga al ponerse la visera.
4. Repetimos el proceso con la otra patilla.

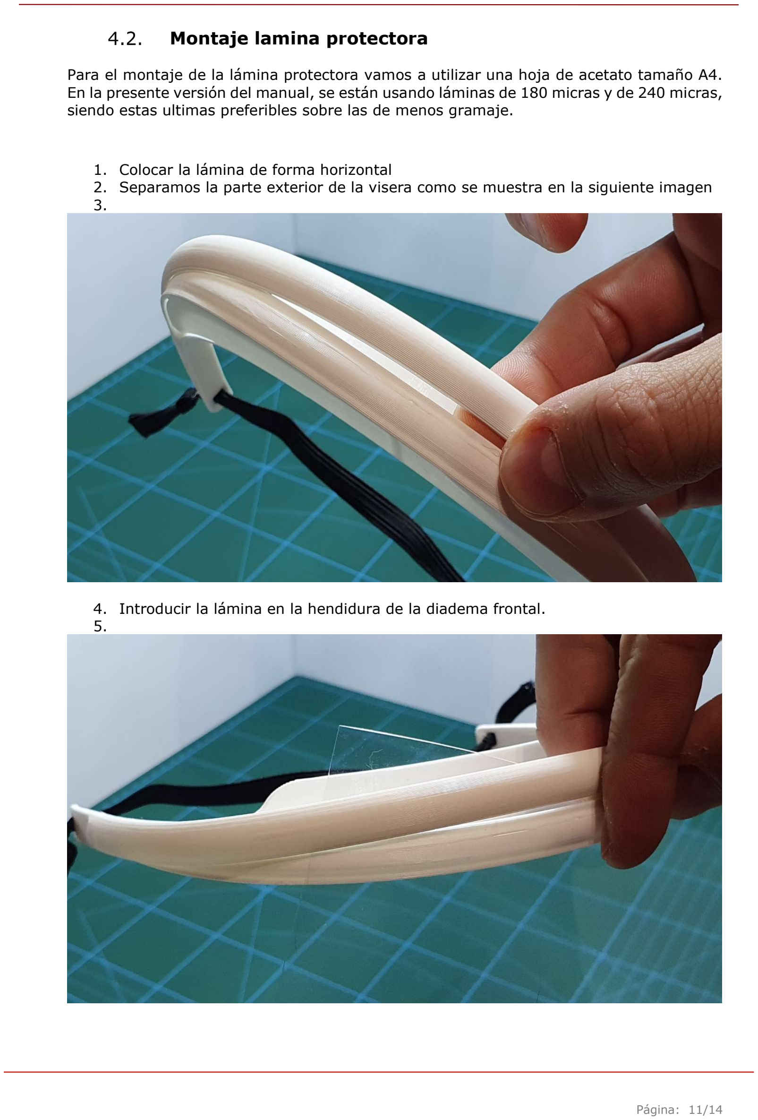
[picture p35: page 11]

Página: 11/14

### Montaje lamina protectora

Para el montaje de la lámina protectora vamos a utilizar una hoja de acetato tamaño A4. En la presente versión del manual, se están usando láminas de 180 micras y de 240 micras, siendo estas ultimas preferibles sobre las de menos gramaje.

### 1. Colocar la lámina de forma horizontal 2. Separamos la parte exterior de la visera como se muestra en la siguiente imagen

3.

4. Introducir la lámina en la hendidura de la diadema frontal. 5.

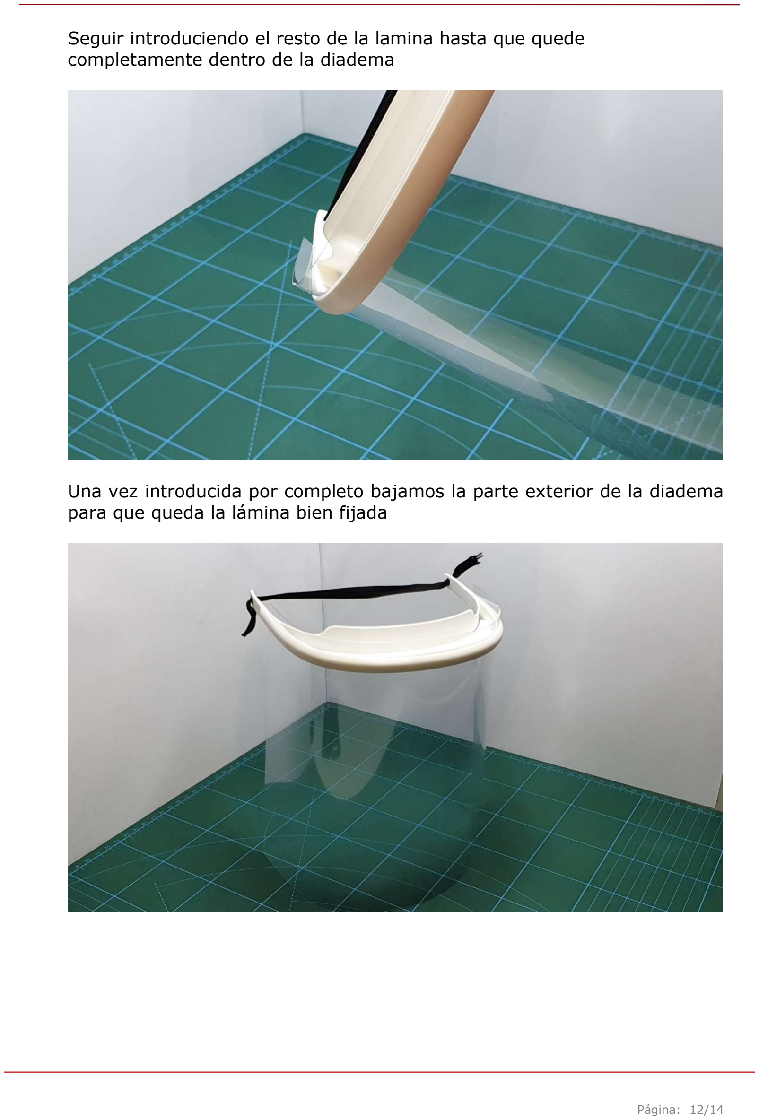
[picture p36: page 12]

Página: 12/14

### Seguir introduciendo el resto de la lamina hasta que quede completamente dentro de la diadema

### Una vez introducida por completo bajamos la parte exterior de la diadema para que queda la lámina bien fijada

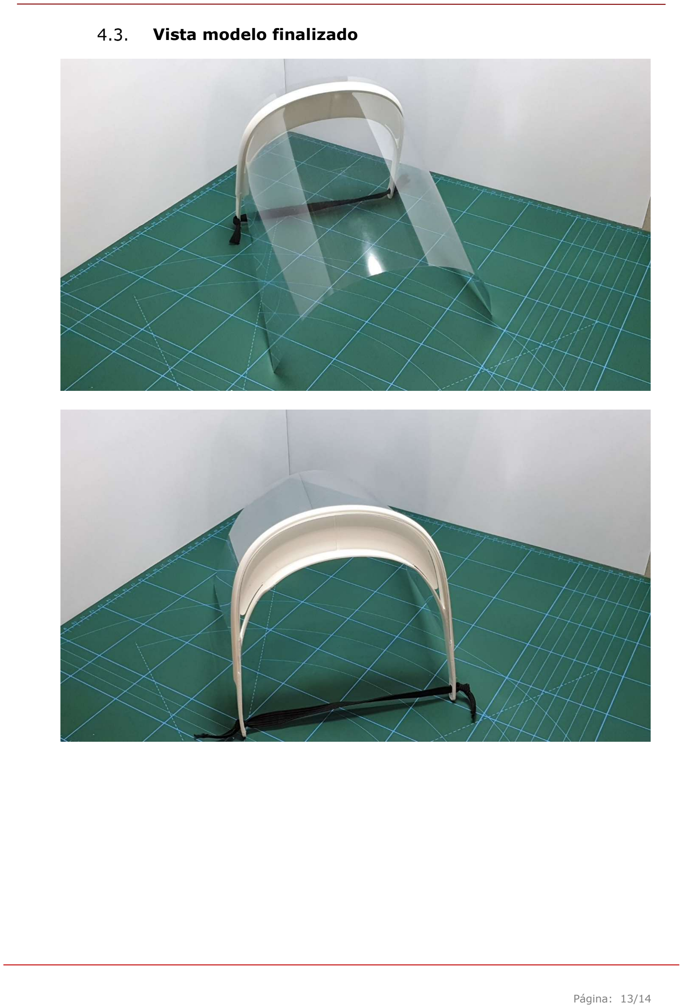
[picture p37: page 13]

Página: 13/14

### Vista modelo finalizado

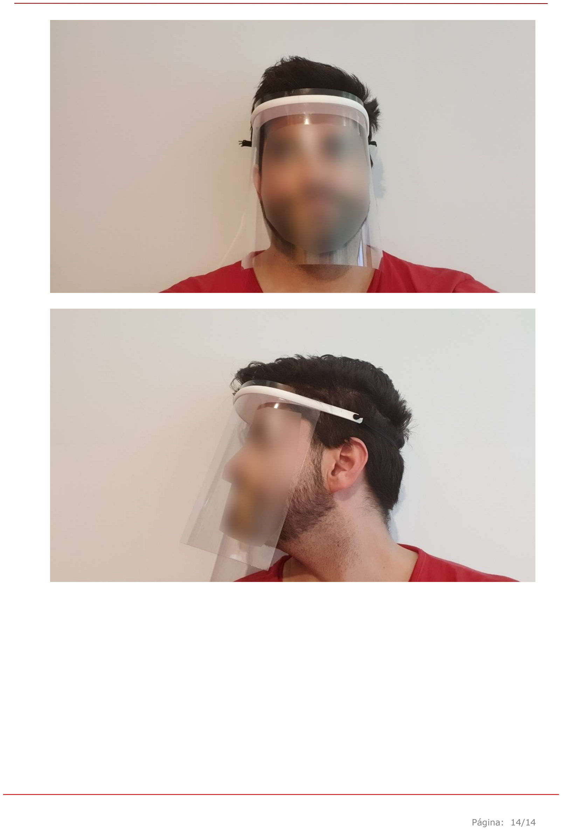
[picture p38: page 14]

Página: 14/14

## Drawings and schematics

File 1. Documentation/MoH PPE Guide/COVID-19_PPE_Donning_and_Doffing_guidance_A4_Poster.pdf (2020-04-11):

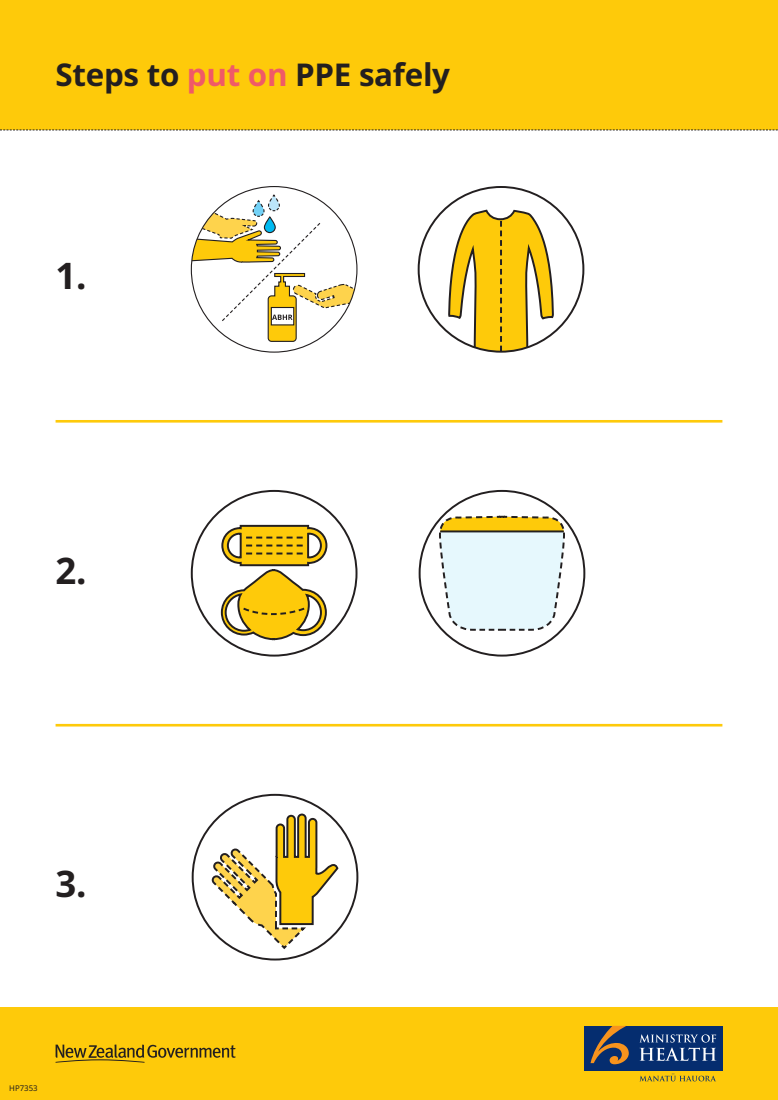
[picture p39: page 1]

Steps to put on PPE safely

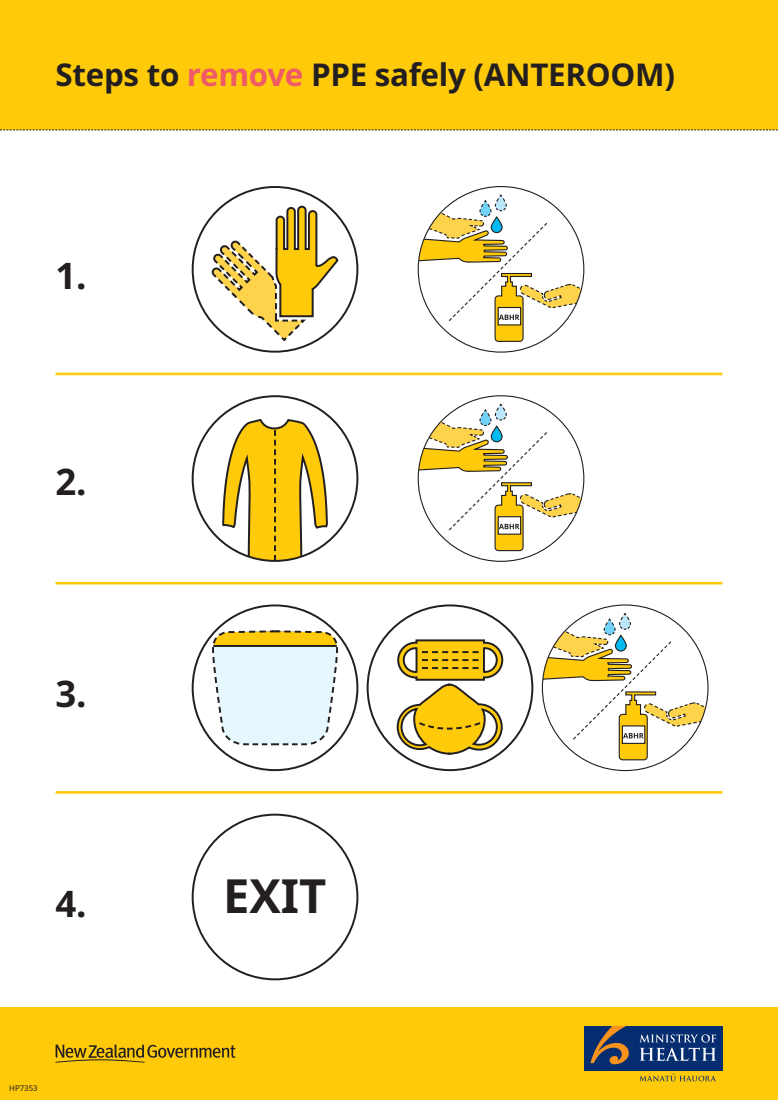
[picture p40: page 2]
4. EXIT

Steps to remove PPE safely (ANTEROOM)

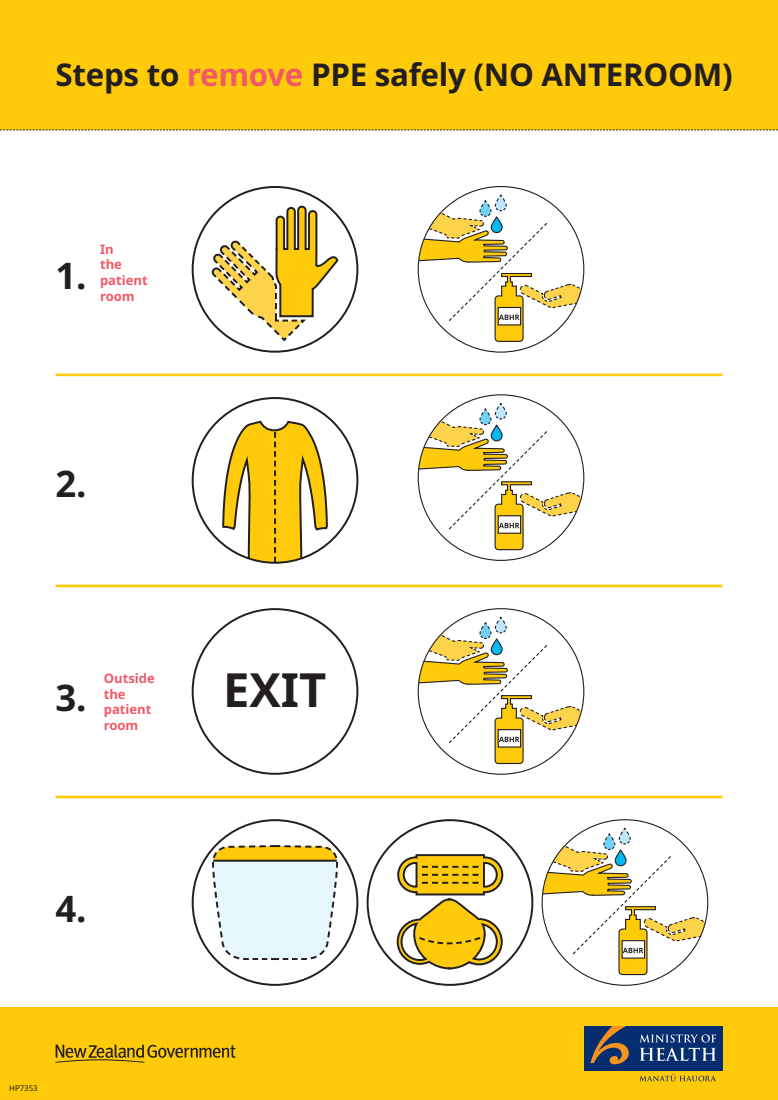
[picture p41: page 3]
3. EXIT; Outside the patient room; In the patient room

Steps to remove PPE safely (NO ANTEROOM)

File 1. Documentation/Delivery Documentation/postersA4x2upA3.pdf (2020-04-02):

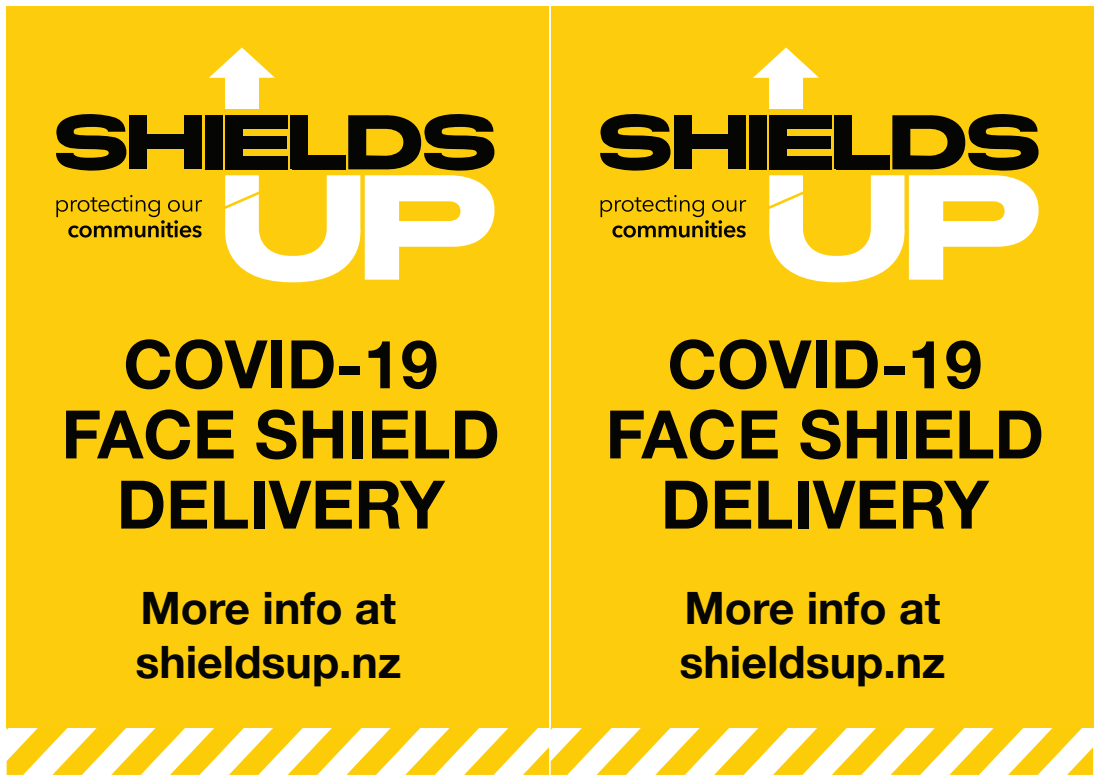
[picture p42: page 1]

COVID-19
FACE SHIELD
DELIVERY
More info at
shieldsup.nz

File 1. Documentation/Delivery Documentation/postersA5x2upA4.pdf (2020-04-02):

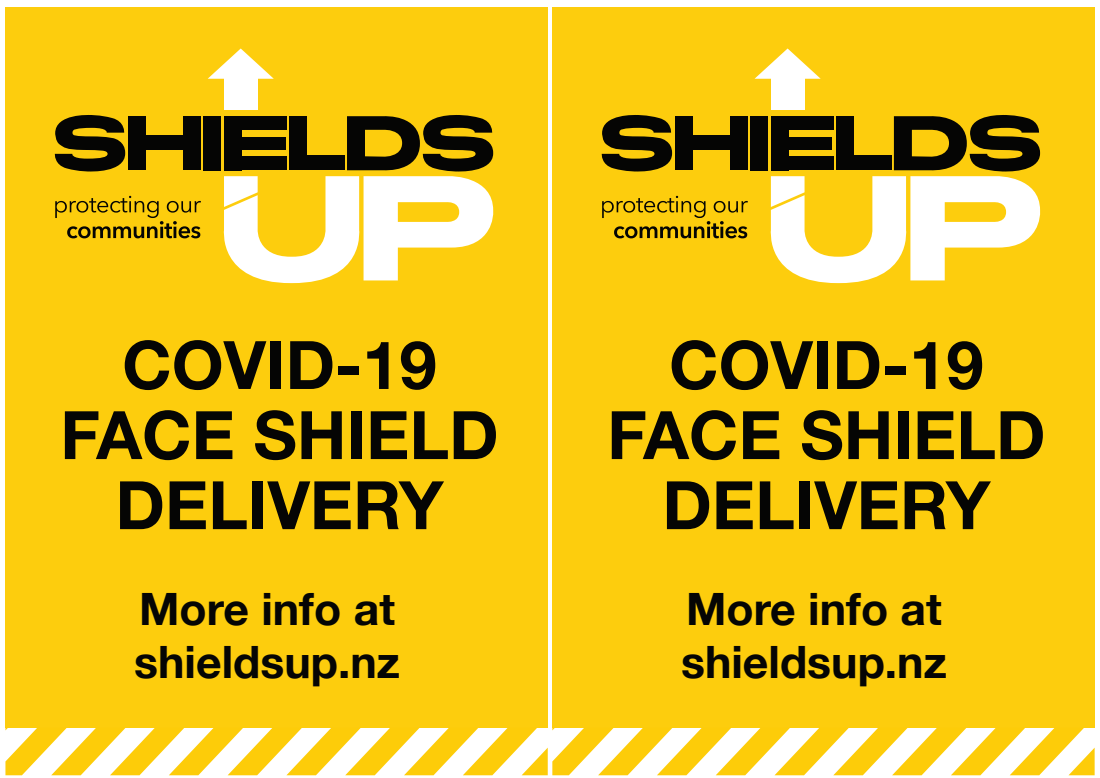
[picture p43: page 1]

COVID-19
FACE SHIELD
DELIVERY
More info at
shieldsup.nz

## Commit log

2020-03-28 Initial file seeding
    [CE3_Shields Up Project - SUP V1.2_0.2_if30_4h58mins.3mf, Shields Up Project - SUP V1.2 - 2xStack (Strong Support).stl, Shields Up Project - SUP V1.2 - 2xStack(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]
2020-03-28 Move-establish printer type folders
2020-03-28 Folder tidy up
    [CE3_Shields Up Project - SUP V1.2_0.2_if30_4h58mins.3mf]
2020-03-28 Sweep up the missed files
    [CE3_Shields Up Project - SUP V1.2_0.2_if30_4h58mins.3mf, rc3-simple.stl]
2020-03-28 Rearrange STL folder
    [Shields Up Project - SUP V1.0.stl, Shields Up Project - SUP V1.2 - 2xStack (Strong Support).stl, Shields Up Project - SUP V1.2 - 2xStack(Easy Remove Support).s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]
2020-03-29 Documentation, Printer settings and Visors
    [CE3_Shields Up Project - SUP V1.2_0.2_if30_B.3mf, CE3_Visera_Plana_con_cierre_y_ventilacion_0.5_0.20_IF30_S.3mf]
2020-03-29 Archives of older designs into zArchive folders.
    [Shields Up Project - SUP V1.0.stl, Visera_Plana_con_cierre_y_ventilacion_0.5.stl]
2020-03-29 DXF Laser Cutter Files for the Prusa Face Shield
    [Shield Array Shared Line_0.50_15 Visors_800x1220.dxf, Shield Array Shared Line_0.50_50 Visors_2440 x 1220.DXF, Shield Array Shared Line_0.75_15 Visors_800x1220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]
2020-03-30 Added print version of instructions, updated DXF files.
    [Shield Array Shared Line_0.50_15 Visors_800x1220.dxf, Shield Array Shared Line_0.50_15 Visors_800x1220_B.dxf, Shield Array Shared Line_0.50_50 Visors_2440 x 12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]
2020-03-30 Renamed folder
    [Shield Array Shared Line_0.50_15 Visors_800x1220.dxf, Shield Array Shared Line_0.50_15 Visors_800x1220_B.dxf, Shield Array Shared Line_0.50_50 Visors_2440 x 12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]
2020-03-30 Adding Frame V2 Stl
    [Shields Up Project - SUP V2 - Final.stl]
2020-03-30 Publishing of V2 STL for the face shield frame
    [Shields Up Project - SUP V1.2 - 2xStack (Strong Support).stl, Shields Up Project - SUP V1.2 - 2xStack(Easy Remove Support).stl, Shields Up Project - SUP V1.2.s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]
2020-03-31 Change licese to reflect project license, non-Commercial use
    COVID-19 Face Shield is licensed under a Creative Commons Attribution-NonCommercial 4.0 International License. This version is by [Jase] on behalf of Shields Up and based on a work by Prusa Research,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
2020-03-31 Updated gcode files
    [CE3_Shields Up Project - SUP V2_0.2_if30_S.3mf]
2020-03-31 Added shield jig for drilling holes
    [Visor_Hole_Jig.STL]
2020-04-01 Added A3 Cut out template
2020-04-01 Updated gcode for PETg creality
    [CE3_Shields Up Project - SUP V2_0.2_if30_S_PETg.3mf]
2020-04-01 Renamed cura profiles
    [CE3_Shields Up Project - SUP V1.2_0.2_if30_B_PLA.3mf, CE3_Shields Up Project - SUP V2_0.2_if30_S_PLA.3mf, CE3_Visera_Plana_con_cierre_y_ventilacion_0.5_0.20_IF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]
2020-04-03 Added face shield cover
    [Shields Up Project - SUP V2 - Final.stl, Shields Up V1.3 - Beta.stl, prusa_protective_face_shield_cover_rc1.stl, rc3-simple.stl]
2020-04-03 Mesh Repair
    Some issues with non-manifold mesh causing slicer problems for some
    users, mesh repaired and issue seems to be resolved
    [Shields Up Project - SUP V2 - 2xStack.stl, Shields Up Project - SUP V2 - 4xStack.stl, Shields Up Project - SUP V2.stl]
2020-04-03 Updated Cura Profiles & Gcodes
    Latest Profiles for Cura as well as a range of code ready to print on
    Ultimaker machines
2020-04-04 Adding the Attach the Visor Video
2020-04-04 Added experimental profiles for Ender 3/3Pro
    [CE3_Shields Up Project - SUP V2_0.3_if0_N_PETg_1up_experimental.3mf, CE3_Shields Up Project - SUP V2_0.3_if0_N_PETg_2up_experimental.3mf]
2020-04-04 Added Open Face Mask to Other Projects
    [OFM-1 Cura Project.3mf, chinarch.stl, frontarch.stl, nosearch.stl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]
2020-04-05 Cura slicer and gcode experimentals for Creality Ender 3.
    [CE3_Shields Up Project - SUP V2_0.27_if0_N_PETg_1up_experimental.3mf, CE3_Shields Up Project - SUP V2_0.3_if0_N_PETg_1up_experimental.3mf, CE3_Shields Up Proje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]
2020-04-05 Ender 3 experimentals, not gone well...
    [CE3_Shields Up Project - SUP V2_1up_0.25_if0_N_PETg_experimental.3mf]
2020-04-05 Update Readme with experimental settings and findings to date
    [CE3_Shields Up Project - SUP V1.2_0.2_if30_B_PLA.3mf]
2020-04-05 Additional printer/filament settings
2020-04-05 Updated Ender 3 print settings
    [CE3_Shields Up Project - SUP V2_1up_0.25_if0_N_PETg_experimental.3mf]
2020-04-05 Sweep Up Ender 3 files
    [CE3_Shields Up Project - SUP V2 - 4xStack_0.25_if0_N_PETg.3mf, CE3_Shields Up Project - SUP V2_1up_0.25_if0_N_PETg.3mf, CE3_Shields Up Project - SUP V2_2up_0.2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]
2020-04-06 Modify ender 3 gcode library
    [CE3_Shields Up Project - SUP V2_2up_0.20_if10_N_PETg.3mf, CE3_Shields Up Project - SUP V2_2up_0.25_if0_N_PETg.3mf]
2020-04-07 Sweep up on ender 3 gcode and Cura files
    [CE3_Shields Up Project - SUP V2 - 4xStack_0.27_if0_N_PETg.3mf, CE3_Shields Up Project - SUP V2_2up_0.27_if0_N_PETg.3mf]
2020-04-11 Updated Design
    Support for the strap mount ‘toggles’ has been simplified for faster
    printing and easier removal, ShieldsUp.NZ branding added for tracking
    our units, non functional design elements removed.
    [SUP V2.1 - 2xStack.stl, SUP V2.1 - 4xStack.stl, SUP V2.1.stl, Shields Up Project - SUP V2 - 2xStack.stl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]
2020-04-11 Rename V2.1 - V2.1-b indicating brim on supports
    [SUP V2.1-b - 2xStack.stl, SUP V2.1-b - 4xStack.stl, SUP V2.1-b.stl]
2020-04-11 Ender 3 CURA/GCODE update to 2.1-b (Brimmed supports). PETg settings added and PLA Settings need testing before use.
    [CE3_SUP V2.1-b - 4xStack_0.27_if0_N_PETg.3mf, CE3_SUP V2.1-b - 6xStack_0.27_if0_N_PETg.3mf, CE3_SUP V2.1-b_0.27_if0_N_PETg.3mf, CE3_SUP V2.1-b_2up_0.27_if0_N_P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]
2020-04-12 File name parameter updated
    [MK3_SUP V2.1 - 10xStack_0.25_if(prusadefault)_none_PETg_9h21mins_E-265C_B-85C(1st layer)_B-90C(remaining).3mf, MK3_SUP V2.1 - 2xFlat_0.25_if(prusadefault)_none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]
2020-04-15 Added visor shield for caps
    [Broche.stp, Frontal.stl, Frontal.stp, Lateral.stl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]
2020-04-25 Added dental frame STL
    [V5.1Dental.STL]
2020-05-05 Added Tiara for Face Shield and tidy up filing
    [IceColdTiara_Gem.stl, Shields Up Project - SUP V2 - Final.stl, Shields Up V1.3 - Beta.stl, Tiara_addon.stl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]
2020-05-11 Addign Dental Stack
    [CE3_V5.1Dental_0.27_if0_N_PETg.3mf]
